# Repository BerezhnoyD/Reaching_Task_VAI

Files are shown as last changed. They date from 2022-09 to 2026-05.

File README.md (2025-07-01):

# ReachOut platform


<p align="center">
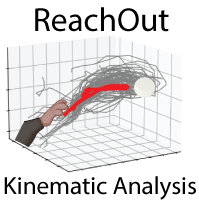
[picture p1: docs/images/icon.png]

</p>

The following project describes the design, fabrication, assembly and use case of the open-source hardware platform for mice reach-to-grasp task training and fine motor skill video analysis. We present the behavioral platform - automated mouse Reaching Box that was designed to be 3D printed and hence easily reproducible. The device is used to train animals to perform reach-to-grasp dexterity task: approach the proximal part of the reaching box and reach for single sugar pellets disposed by motorized feeder disk located in front of the narrow slit. 
This task is used for studying planning and execution of fine motor skills requiring cortical control of the forepaw and finger movement. Behavioral apparatus allows to record the video and track the forepaw and fingers during the reaching movement. Tracking data (performed by DLC networks) can be analyzed further to extract different kinematic parameters (speed, acceleration, jerk, accuracy) and different moments of the reach (start, peak, end) to use them as behavioral keypoints (ex. peri-event analysis).

This repository is accompanying the STARs protocol article describing the fabrication and use of the setup

[Open-source platform for kinematic analysis of mouse forelimb movement](https://star-protocols.cell.com/protocols/3539)

For even more details on installation and use of the Software/Hardware platform visit the 
[Docs Website]

<br>

[][Docs Website]

<br>

The website contains all the documentation and repository contains all the materials to build the mouse reaching task and analyze the data acquired with this task
- *Schematics and blueprints* to assemble the components 
	(**/Article Supplements/**)
- *3D models* for the components of the box 
	(**/ReachingBox_3D_Model/**)
- *Scripts to run the video recording* from the FLIR Camera and logging the data from Arduino 
	(**/Recording toolbox/**)
- *Scripts for the full analysis* dataflow: detecting body parts with DLC and getting the reaching trajectories 
	(**/Analysis toolbox/**)

___

## Installation
***ReachOut*** pipeline can be used with the **behavioral box** to analyze reaching kinematics or as a **standalone application** for kinematic
analysis for the action of your choice (walking, whisker movement, you name it) with certain adaptations. In both cases you
will need to install some software components on your recording/analysis computer. We split the scripts used to two toolboxes with different purpose.

### Recording toolbox
The recording toolbox contains two parts: 
- one on the **Arduino** side (Choose one script from */Arduino/* folder of the repository and uploaded to the microcontroller with the use of **Arduino IDE**). 
- and one on the **PC** side. This Python CLI program is used to record simultaneously from the FLIR camera and from Arduino. 
There are two different programs that can be copies from */FLIR_CPU/* folder of the repository. This part is taken with minor changes from the [PySpin repository], so you should follow the additional instructions listed there. 
We also provide installation instructions on our [Docs Website].

### Analysis toolbox
All the code for analysis toolbox is compiled in the /2D pipeline/ folder. To run different steps of the analysis just run
one of the *ReachOut Notebooks* [^1].
Analysis toolbox is dependent on different Python libraries (ex. DEEPLABCUT, ANIPOSE) and Jupyter Notebook [^2].
DEEPLABCUT (https://github.com/DeepLabCut/DeepLabCut)
ANIPOSE (https://github.com/lambdaloop/anipose)

To make it easier for installation all the dependencies are included in the included **DEEPLABCUT.yml** conda environment file [^3].

___

[^1]: Small library of classes and functions needed to run the kinematic analysis is contained in the *.py files in the same directory and you imported in Notebooks themselves.
[^2]: If you just want to use the Analysis and Visualization notebook on your analyzed videos it should work even in the base Anaconda environment without DLC/Anipose installed. 
[^3]: There are known copmatibility problems on some PCs with the installation of new DLC version that we are trying to fix. Please contact us with any problems you experience.
___
### Troubleshooting

Feel free to read our [Docs Website] and if you still have questions submit a request here or contact the developer directly. 
Contribute, star this repository if you use it and submit an issue for any questions. Let's make it better together.

___

[Docs Website]: https://berezhnoyd.github.io/Reaching_Task_VAI/
[PySpin repository]: https://github.com/neurojak/pySpinCapture
[berezhnoyd.github.io]: https://img.shields.io/badge/Visit_berezhnoyd.github.io-37a779?style=for-the-badge

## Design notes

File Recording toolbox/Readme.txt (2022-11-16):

This folder contains all the programs needed for the behavioral box to work and acquire data.
- Arduino programs for the box controller (in a separate Arduino folder)
- Scripts to run on the computer (in a separate FLIR folder, modified from the PySpin repository)

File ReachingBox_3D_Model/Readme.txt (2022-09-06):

This folder containst all the files needed to built the reaching box:
- 3d files + stl files for printing the plastic angles to hold the Plexiglas sheets together
- 3d files + stl files for mirror hinges (we experimented with different angles so all the angles provided)
- 3d files + stl files for the rotating disk feeder
- blueprints of the plastic sheet dimensions and the overall box

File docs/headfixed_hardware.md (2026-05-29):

---
layout: page
title: Headfixed hardware
parent: Bonus Headfixed setup
nav_order: 7
description: "This is a description of hardware for headfixed setup"
---

# Behavioral setup design

Current protocol is performed with the use of two different systems (shown in the picture below). The one on the right was purchased through [Labeotech](https://www.labeotech.com/product/mouse-head-fixation/),
and the one on the left manufactured in-house using mostly the parts from [ThorLabs](https://www.thorlabs.com/). The list of materials can be found in the source table in the
repository. It should be noted that the first system is designed for the head fixation using the small titanium bars affixed to the skull, while the second is fitted for
the use of headplates, which gives more flexibility in implant design. The second system is easily regulated in height and also can be used for different tasks beyound reaching (ex. rotarod).
 
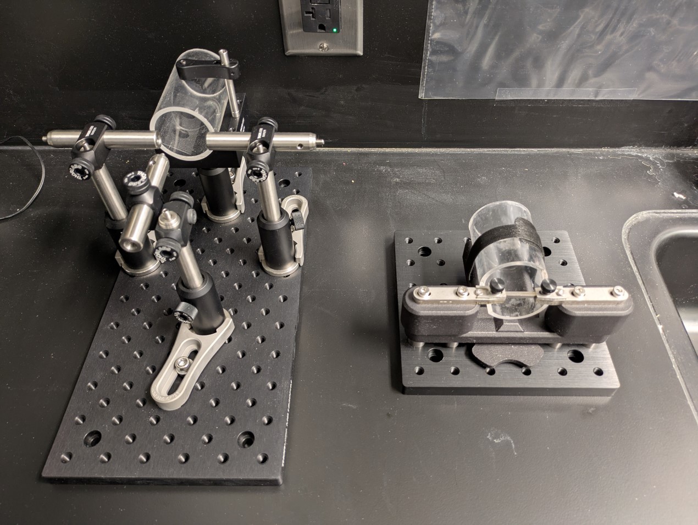
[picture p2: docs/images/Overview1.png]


The system consists of three principal components: 
- Head fixation device with a plastic tube, housing the mouse during the experiment; 
- Motorized water delivery system - linear actuator syringe pump and an XY moving stage with a blunt needle;
- Arduino-based controller performing the programmed experimental protocol (written in C++), interfacing with the touch sensors in the box and providing the master clock signal

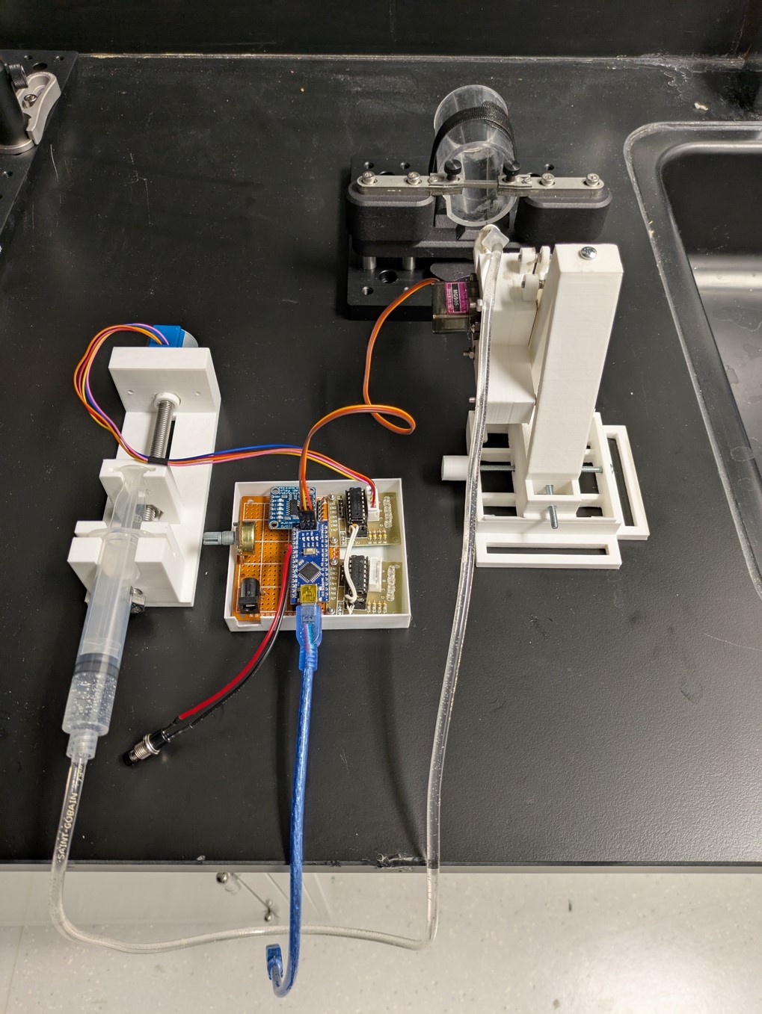
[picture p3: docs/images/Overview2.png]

***The view of the whole system with actuator, water delivery and the controller schematic***

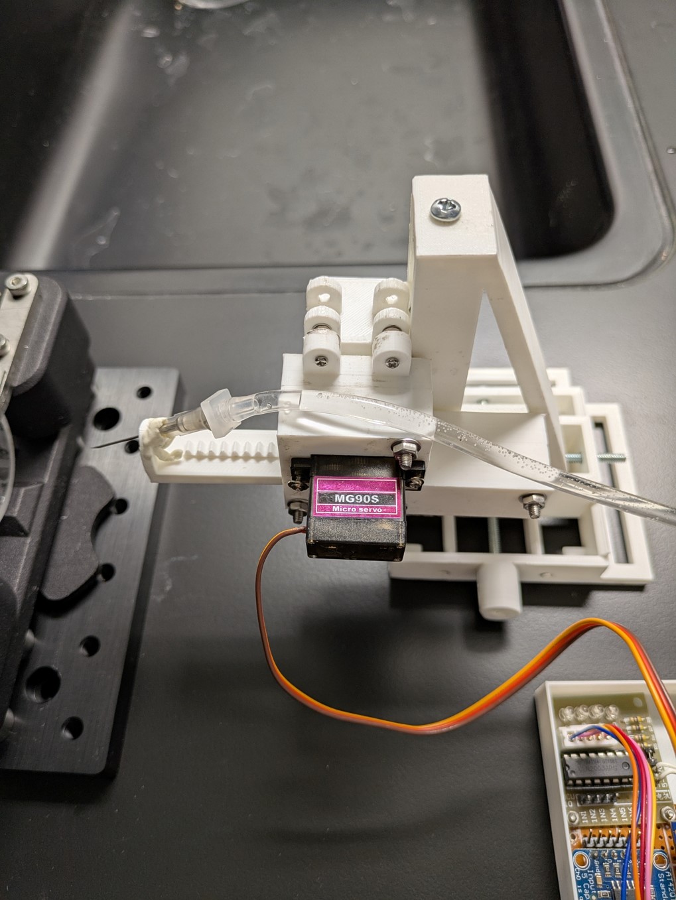
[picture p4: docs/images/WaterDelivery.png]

***Close-up on the water delivery tip on the XY actuator***

The whole water delivery system is 3D printed *.stl* files for printing the plastic components are provided in [this folder] of the repository. You will also need long M2 screws and nuts
to fabricated the metal shafts for XY actuator and M5 screw for the water pump actuator (as a "rail" to move the syringe plunger). 

## Assembly

The custom system is assembled on the optical posts from Thorlabs, which are mounted on the solid heavy base. Two rods mounted perpendicularly are used for holding the head and
are fitted with 3D printed holders for headplates. 
The design for both headplates and the holders can be found in [that folder] of the repository. While holders are 3D printed and simply screwed on the pin of the optical post, 
to manufacture the headplates you will need a laser cutter. If you don't have one you can simply upload the models to one of the online cutting services like [SendCutSend](https://sendcutsend.com/).

The electrical part of the device is largely overlapping with the original ReachOut project (see schematic in the "Hardware part") and is based on the ***Arduino Nano*** 
with two main periferal boards from Adafruit: 
 - ***ULN2003 board*** to control a small BYJ48 stepper motor in the syringe pump
 - ***AT42QT1070*** board connected to the blunted syringe needle to detect touches

***Optional***:  there is also an optional actuator for the syringe needle which is motorized using MG90S servo motor directly connected to Arduino (zoom the picture above for more details).

## Code

As the heart of our training setup is the water delivery system, and it is controlled by Arduino, all the protocols are framed as different programs that can be uploaded on the device.
Those protocols can be found in [code folder] of the repository:
 - HeadFixed_Program
 - HeadFixed_Program_Auto
 - HeadFixed_Program_Manual

There is also some code that can be used if you try to build a headfixed rotarod (based on the rotary encoder with Arduino) with this setup.

[this folder]:(https://github.com/BerezhnoyD/Reaching_Task_VAI/tree/main/HeadFixed_Setup/WaterDelivery/Water_delivery_3d_models/)
[that folder]:(https://github.com/BerezhnoyD/Reaching_Task_VAI/tree/main/HeadFixed_Setup/Headplate_designs/)
[code folder]:(https://github.com/BerezhnoyD/Reaching_Task_VAI/tree/main/HeadFixed_Setup/WaterDelivery/Water_delivery_code/)

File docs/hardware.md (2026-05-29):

---
layout: page
title: Hardware part
nav_order: 3
description: "This is a description of ReachOut behavioral box electronics"

---

## Hardware overview

Here is the design of the whole setup, everything on the box side is controlled by **Arduino**,
and the experiment can be performed event without the the computer, but you will need **the PC** to 
save the streaming data from the camera and the box sensors.  

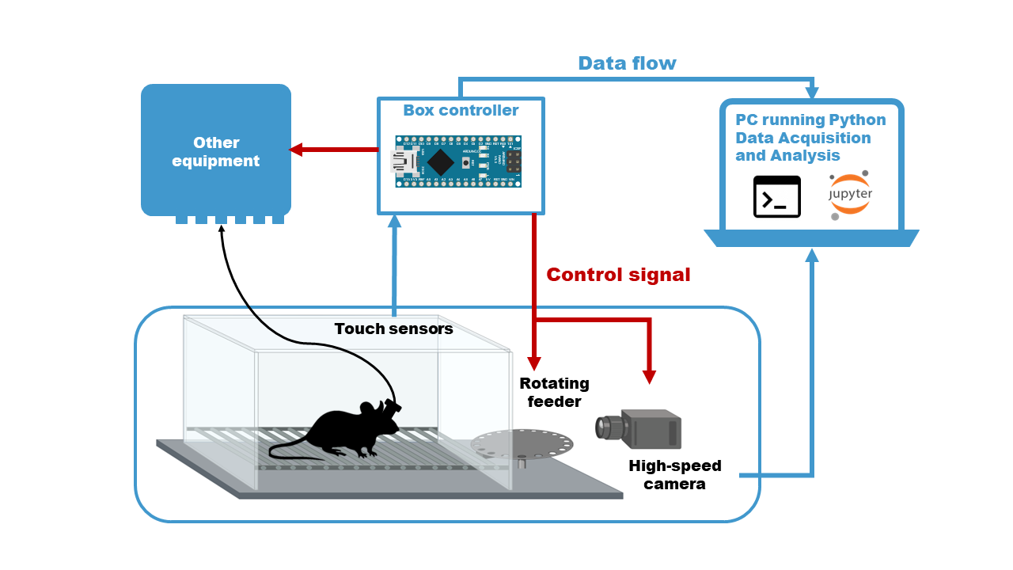
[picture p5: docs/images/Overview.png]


The **control** of the behavioral protocol, all the **stimuli** and **reinforcement** (food pellets) presentation, 
**data logging** from the sensors and video camera stream activation is handled by the custom circuit, connected to all the components of the reaching box. 
The schematics are housed in a small 3d printed box and soldered together on a simple breadboard. Most of the components are ready available cicuit modules, which
you just need to put together (no extensive knowledge of electronics needed).

## Main circuit components

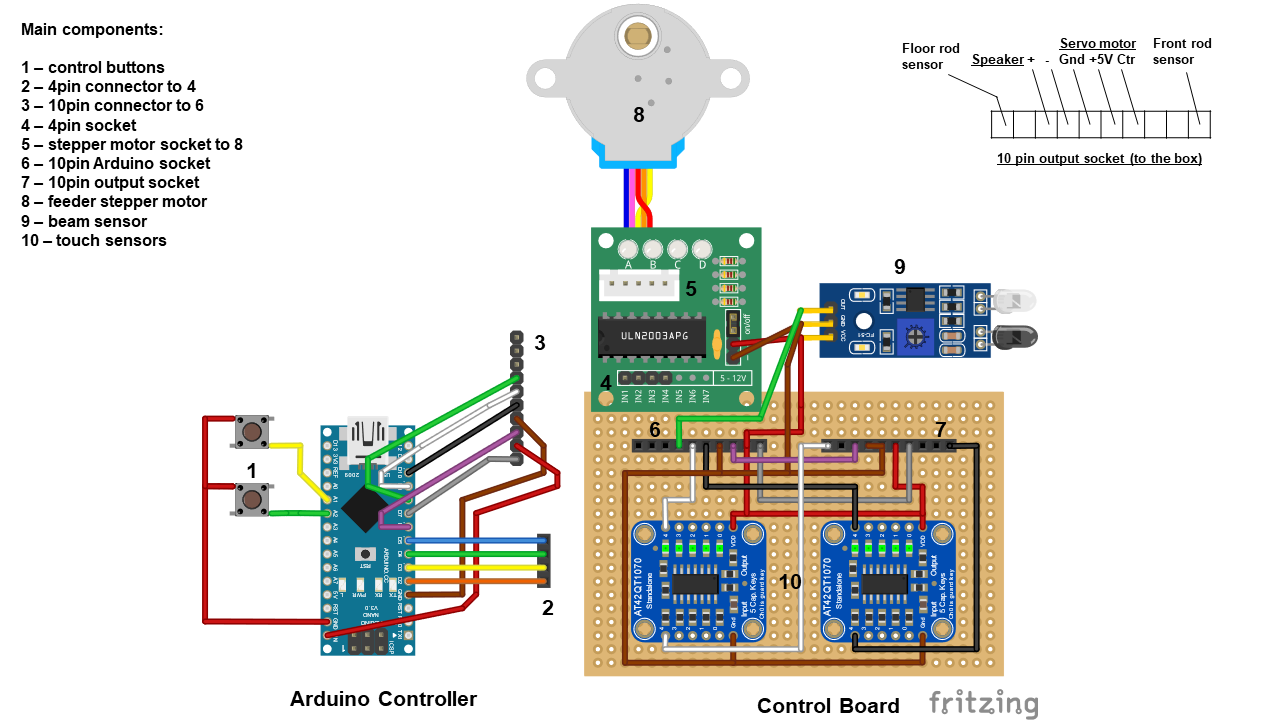
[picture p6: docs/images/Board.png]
  

The same schematics can be found in the Repository and [STAR Protocols] article, supplementary materials.
The main components of the system are the **Arduino Nano** controller autonomously performing the programmed experimental protocol (written in C++ using Arduino IDE) 
with different **Adafruit shields** connected to it. Hence, powered with an external 5V source this behavioral system can be used autonomously for automatic/semi-automatic 
training of mice to perform the reach-to-grasp task, freeing the experimenter from the manual handling of behavioral protocol, and allowing seamless integration with 
*in vivo* electrophysiology recording or other current brain recording/stimulation methods. 

At the same time, connected to the **computer with a USB cable** and a simple 
**Python program** on the computer side this system saves two data streams and allows live monitoring of the data: basic behavioral data from the touch sensors 
(position of the animal, paw placement, time spent in front of the slit, timing and number of trials) and 3d view of the reaching movement (from the front camera and two side mirrors) 
that allows for more sophisticated kinematic analysis of both left and right-hand reaches. 

## Uploading the experimental protocol

The assembled box is programmed with [Arduino IDE] for its use as a standalone device for automated/semi-automated
animal training and behavioral data acquisition. The reaching box can log basic behavioral data (touch/beam sensors)
and is designed to be connected to external devices to trigger in vivo imaging, optogenetic stimulation etc. 
It can stream the synchro signal from the behavioral events recorded by the onboard sensors with millisecond resolution,
which makes it ideally fitted for synchronized behavioral-neurophysiology experiments. With the use of multiple mirrors, 
the system can acquire multiple close-up views for 3d trajectory reconstruction (triangulation) of the reach-to-grasp movement 
with a single high-speed **FLIR camera** when connected to the **desktop PC**. The output of the system is a behavioral video of the 
reaching movements throughout the learning session along with the *.tsv* table of the synchronized data from **Arduino**. 

After a single upload of the program the board will perform it autonomously on every power up without any actions needed from the user. 
To switch to another protocol, we’ll need to upload another program using Arduino IDE. The Arduino programming environment can be downloaded from the
official website [Arduino IDE] and is used to write compile and upload the C++ code for Arduino controllers. 

### List of the programs provided in the repository:
 
1.	***Reaching_Task_Draft*** – basic protocol with initialization for all the components to explore the structure of the program.
2.	***Reaching_Task_Manual*** - Feeder makes one step clockwise or counterclockwise when the experimenter presses the left or right button respectively.
3.	***Reaching_Task_Feeder_Training*** – Feeder takes one step every 10sec while animal is in the front part of the box.
4.	***Reaching_Task_Door_Training*** – If animal is detected in the front part of the box and grabs the elevated front rod, the feeder takes one step and the door blocking the slit opens (need additional servo motor connected, see Fig.3D).
5.	***Reaching_Task_CS_Training***  - If animal is detected in the front part of the box the speaker delivers 5s beep sound (CS trial) with intertrial intervals of 5s (ITI) and if the animal grabs the elevated front rod during this sound (trial) the feeder makes one step and the door blocking the slit opens

## Q&A

If you still have questions after reading this and [STAR Protocols] please let us
know and we list it in this section.

---

[STAR Protocols]: https://star-protocols.cell.com/protocols/3539
[Arduino IDE]: https://www.arduino.cc/en/software

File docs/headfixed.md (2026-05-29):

---
layout: page
title: Bonus Headfixed setup
nav_order: 6
description: "This is a description of the HeadFixed Reaching setup (ReachOut v.2.0)"
has_children: true

---

# ReachOut v.2.0 (Headfixed setup for reaching and treadmill activity)



As a follow-up to the ReachOut project we have developed its full ***headfixed*** counterpart, which we ended up never using. 
But as a bonus here we provide all the details of this side project in a good spirit of open science. We have added a
corresponding section to the original GitHub repository (**/Headfixed_Setup**) and all the contents are described here. Feel free
to hit us with any questions that might save you the trial-and-error process we went through.

## Project overview

The ***contents*** of the project folder in GitHub repository:
 - **WaterDelivery**
	- /Water_delivery_3d_models/ (all the models you need for the water delivery system: DIY pump and actuator)
	- /Water_delivery_code/ (various Arduino programs corresponding to different protocols)
	- /Water_delivery_pictures/ (pictures showing the overview of the system, also Materials Source table) 
	- /Water_delivery_tests/ (pictures and tests for the system)
 - **Headplate designs** (the designs for the headplates for head fixation, modified after A.Ribic [^1] lab)

The ***following sections*** lead you through different parts of the setup: 
 - Hardware, 
 - Electrical Components, 
 - Code to run the protocol, 
 - Device testing and animal training  

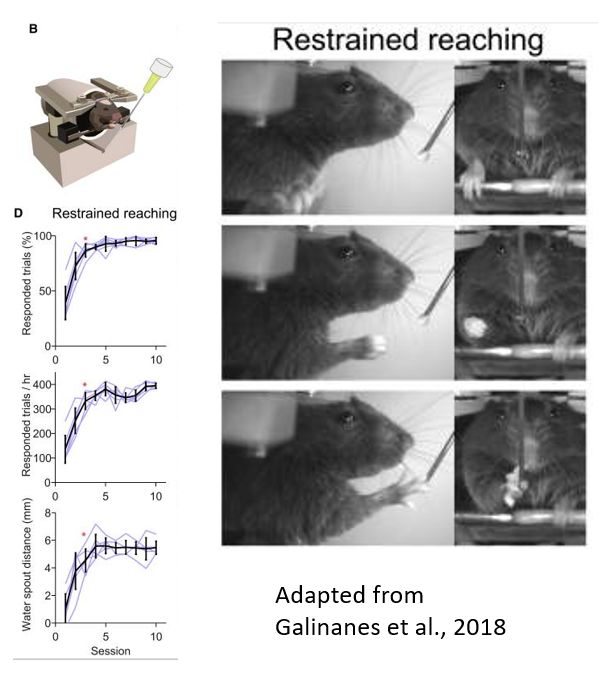
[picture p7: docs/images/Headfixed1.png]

 
This setup allows you to study cortical circuitry of the reaching movement in more detail using 2-photon microscopy or
other methods requiring more stability than you can achieve with freely moving behavior. It is heavily inspired by the one from 
Galinanes 2018 article [^2] and Carlsen 2022 article [^3] so for further details we point you to their work. 
In short, animal is fixed by the head with only the forepaws freely moving, and the water reinforcement is delivered through 
a blunt syringe needle within reaching distance. The distance is gradually increased during training
and the position of the needle changed to shape the proper directional response. 

## About the project

ReachOut is maintained &copy; 2022-{{ "now" | date: "%Y" }} by [Daniil Berezhnoi](https://www.linkedin.com/in/daniil-berezhnoi-a4039844/).
All the materials are OpenSource and Authors would be happy to help you with any questions on the code.

----

[^1]: [Headplate designs from the Ribic lab](https://ribicneurolab.com/headplate-designs)
[^2]: [Directional Reaching for Water as a Cortex-Dependent Behavioral Framework for Mice](https://pubmed.ncbi.nlm.nih.gov/29514103/)
[^3]: [Versatile treadmill system for measuring locomotion and neural activity in head-fixed mice](https://www.sciencedirect.com/science/article/pii/S2666166722005810)

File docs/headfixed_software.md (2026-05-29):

---
layout: page
title: Headfixed software
parent: Bonus Headfixed setup
nav_order: 8
description: "This is a description of software and testing for headfixed setup"
---

# Testing the setup

Initially we have tried to follow the protocol from the Galinanes 2018 article [^1], which includes
gradual shaping of the spontaneous reaching/licking response to water in water-deprived animals. For us
the success of the protocol heavily depended on the level of animal handling (stress response to head restraint),
motivation (water deprivation) and individual differences and the % of animals learned was never more than 50.
Here is the schematic of our initial learning protocol.
 
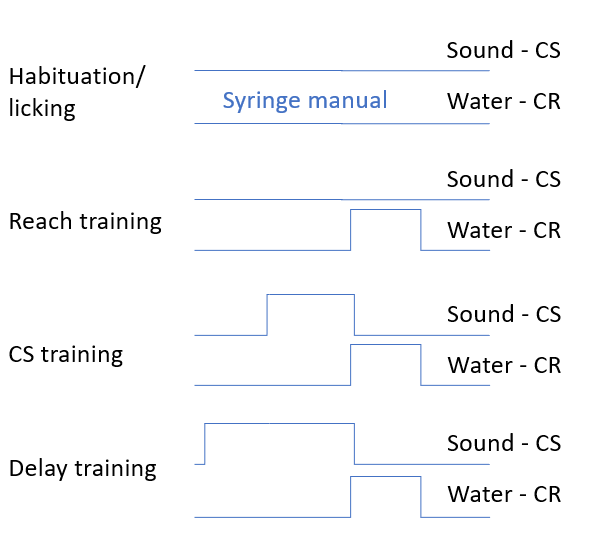
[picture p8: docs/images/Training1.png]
 

Hence, we had to switch to another way of evoking the reaching response that depended less on the internal animal state
and other variables. We actually found the "Pavlovian" way (relying on the innate reaction) to induce reaching more consistent in our hands. 
The innate paw reaction, e.g. grooming/washing response, was consistently induced by touching animal whiskers with the water droplet being delivered.
This reaction, thought initially far from the purposeful reaching for water, can be transformed into a skilled response by the same shaping approach
as was employed in Galinanes 2018 article [^1]. Hence our final protocol looked like this.

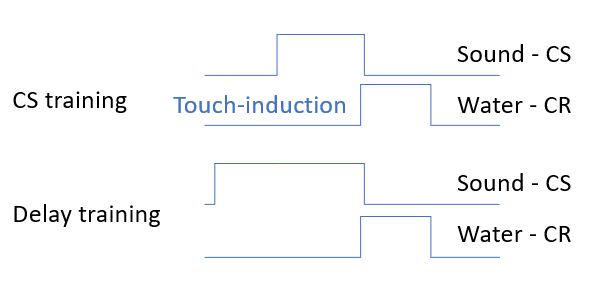
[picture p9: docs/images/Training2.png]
 

## Videos showing different optimization steps 
In the following videos you can see various stages of the protocol and device testing that may give you insights on how to implement the protocol. 
***Note*** that before starting the training protocol animal should be handled and accustomed to the experimenter, to water deprivation, to being restrained in the 
behavioral setup, and licking water from the syringe tip. The device and the protocol should be extensively tested before starting any actual animal work.

First step is to test the water delivery system and determine the optimal ~20-50mkl size of the water droplet before starting any animal work (adjusting the number
of stepper steps and the syringe size mounted in the pump)
<iframe width="600" height="600" src="{{ site.baseurl }}/images/Water1.mp4" frameborder="0" allowfullscreen></iframe>

The goal of the second step is to determine the optimal distance from the snout to the syringe tip (~5mm) to induce the licking and reaching responses
(generally the key is to touch the whiskers at first as it induces the grooming/washing response, and then gradually increase the distance). 
<iframe width="600" height="600" src="{{ site.baseurl }}/images/Water2.mp4" frameborder="0" allowfullscreen></iframe>

The actual training should be performed only when the animal has a stable reaching response and is devoted to pairing up conditioned stimulus (buzzer,
here paired with an LED for illustrative purposes) with the response.
<iframe width="600" height="600" src="{{ site.baseurl }}/images/Water3.mp4" frameborder="0" allowfullscreen></iframe>

----

[^1]: [Directional Reaching for Water as a Cortex-Dependent Behavioral Framework for Mice](https://pubmed.ncbi.nlm.nih.gov/29514103/)

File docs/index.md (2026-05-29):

---
layout: home
title: Home
nav_order: 1
description: "Documentation for the ReachOut project"
permalink: /
---



ReachOut project is an open-source hardware-software platform for analyzing reaching movement kinematics in mice. 
The whole design consists of 3 main parts described here:
{: .fs-6 .fw-200 }
- ***3D printed box*** for training mice to perform reach-to-grasp task & acquire behavioral videos for kinematic analysis
- ***Arduino-based controller*** for executing behavioral protocol & recording animal behavior
- ***ReachOut software (analysis pipeline)*** to analyze videos & perform kinematic analysis on reconstructed forepaw trajectory
{: .fs-6 .fw-200 }


There is an Article in STAR Protocols with all the details and Repository on GitHub with all materials
to recreate the setup
{: .fs-6 .fw-200 }
[View it in the Article][STAR Protocols]{: .btn .btn-primary .fs-5 .mb-4 .mb-md-0 .mr-2 }
[View it on GitHub][ReachOut]{: .btn .fs-5 .mb-4 .mb-md-0 }
 
{: .warning }
> This website documents the features of the current `main` branch accompanying the STARs Protocol article. For the code described in the article use
> alpha or beta release in the [ReachOut] repository

---

### Getting Started
Did you know that mice are pretty good at using their forepaws? Well, probably you do
and can skip the [Science background](#science-background) section and go straight to [Project overview](#project-overview)
or to one of the sections provided in the docs (*Navigation on the left sidebar*).



But how to dissect and study this complex movement? 
We tried to provide the comprehensive solution to this problem that can be
implemented in-lab with a little background knowledge in *3d printing, Arduino and Python Coding*.
  
All the installation instructions are currently in the [Software part](#software.html) section. 
You can use the analysis part separately for your project by copying the Jupyter Notebooks.

### Science background
Reach-to-grasp task in rodents first developed by Ian Whishaw [^1] has recently became the gold standard for the study of fine motor behavior in rodents.
The structure of the movement and the neurocircuitry behind it can be well translated between rodents and higher primates including humans [^2][^3] which makes this task
very popular for the study of cortical motor control. There is an increasing use of reach-to-grasp task along current neurophysiological tools like 2-photon imaging
or optogenetics for the study of neural activity during execution of the planned motor command [^4]. However, there are not many designs available for the reach-to-grasp task in freely behaving mice. 

With the dawn of DIY electronic kits (**Arduino**) and stereolithography 3D printer technology (**OpenCAD**) we see the field of open-source behavioral box design rapidly expanding and
being a major driver for neuroscience discoveries. There are multiple designs for Skinner boxes and rodent operant chambers proposed by different laboratories. However, there are fewer 
solutions to study fine motor skills, probably due to the difficulties in *precise presentation of the reinforcement* and *quantifying the kinematics* of the small animal movements. 
The second problem has been recently solved with the use of deep-learning video analysis [DeepLabCut]. However, the solutions specifically tailored for the behavior-neurophysiology coupling often use
head-fixed animals and focused on precise synchronization of the animal behavior, heavily constrained, with the neurophysiology recording. 
Training animals in such setups can be *problematic and labor-intensive*. On the other side, apparatuses proposed to study reaching in freely behaving animals, 
following the line of operant boxes research, usually lack the precision and time resolution needed to synchronize with external devices used in neurophysiology research. Moreover, research with 
automatic learning boxes, even ReachingBots [^5], generally focus on simple metrics like the number of trials and success rate of reaching and overlook more sophisticated kinematic analysis which requires better video quality, 
precision and post-processing of the behavioral data. Thus, there is always a tight balance between the *open-source (ease of manufacture)* and *research-grade (temporal precision)* needed for neurophysiology 
and precise kinematic studies.
  
***Trying to fill this gap we have developed a comprehensive hardware-software setup for mice, using the current state-of-the-art solutions in 3D printing and DNN data analysis and made it accessible to the large open-science community.***

### Project overview
This website describes the basics of design, fabrication, assembly and use case for the open-source hardware platform
for mice reach-to-grasp task training and fine motor skill video analysis. You are free to use either the [Software part](#software.html)
of this project for kinematic analysis ***(ReachOut pipeline)*** on the videos from your setup or build the whole behavioral apparatus setup 
using the instructions provided in the [STAR Protocols] article.

***Behavioral apparatus*** - automated mouse Reaching Box that is 3D printed and hence easily reproducible. 
The device is used to train animals to perform reach-to-grasp dexterity task: approach the proximal part of the reaching box
and reach for single sugar pellets disposed by motorized feeder disk located in front of the narrow slit. 
This task is used for studying planning and execution of fine motor skills requiring cortical control of the forepaw and finger movement. 
The semi-automated setup allows to record the video and track the forepaw and fingers during the reaching movement. 

***Hardware*** used in the design of the task, aside from the high-speed FLIR camera, 
consists of readily available open-source components that can be acquired relatively 
cheap or fabricated with the use of stereolithography 3D printer. 

The [ReachOut] repository contains all the materials to build the mouse reaching task and analyze the data acquired with this task
- 3D models for the components of the box
- Schematics for the reaching box Arduino-based controller
- Scripts to run the video recording from the FLIR Camera and logging the data from Arduino
- Scripts for the full analysis dataflow: detecting body parts with DLC and getting the reaching trajectories

***Analysis software*** can be used with the behavioral box to analyze reaching kinematics or as a standalone application for kinematic
analysis for the action of your choice (walking, whisker movement, you name it) in your project with certain adaptations. The aim of this part
is to simplify keypoint tracking (performed by DLC networks), reviewing tracking results along with the videos and extract different kinematic parameters 
(speed, acceleration, jerk, accuracy) and different moments of the reach (start, peak, end) to use them as behavioral keypoints (ex. peri-event analysis).

We gathered all the code in a series of annotated [Jupyter Notebooks] for you to use. All the necessary
libraries can be installed using provided *DEEPLABCUT.yml* environment file for **Anaconda**.
For the quick overview and instructions go straight to [Software part](#Software part) section.

## About the project

ReachOut is maintained &copy; 2022-{{ "now" | date: "%Y" }} by [Daniil Berezhnoi](https://www.researchgate.net/profile/Daniil-Berezhnoy).
All the materials are OpenSource and Authors would be happy to help you with any questions on the code.

----

[^1]: [The structure of skilled forelimb reaching in the rat: A proximally driven movement with a single distal rotatory component](https://www.sciencedirect.com/science/article/pii/016643289090053H#:~:text=(1)%20Most%20of%20the%20first,the%20midline%20of%20the%20body.).
[^2]: [Post-stroke kinematic analysis in rats reveals similar reaching abnormalities as humans](https://www.nature.com/articles/s41598-018-27101-0)
[^3]: [Quantitative kinematic characterization of reaching impairments in mice after a stroke](https://pubmed.ncbi.nlm.nih.gov/25323462/)
[^4]: [Online control of reach accuracy in mice](https://www.ncbi.nlm.nih.gov/pmc/articles/PMC7814908/)
[^5]: [ReachingBot: An automated and scalable benchtop device for highly parallel Single Pellet Reach-and-Grasp training and assessment in mice](https://www.sciencedirect.com/science/article/pii/S0165027023001279?via%3Dihub)

[STAR Protocols]: https://star-protocols.cell.com/protocols/3539
[DeepLabCut]: https://github.com/DeepLabCut/DeepLabCut/
[Anipose Lib]: https://github.com/lambdaloop/aniposelib/
[ReachOut]: https://github.com/BerezhnoyD/Reaching_Task_VAI/
[Jupyter Notebooks]: https://github.com/BerezhnoyD/Reaching_Task_VAI/tree/main/Analysis toolbox/2D pipeline/
[Just the Docs]: https://just-the-docs.github.io/just-the-docs/
[GitHub Pages]: https://docs.github.com/en/pages
[README]: https://github.com/just-the-docs/just-the-docs-template/blob/main/README.md
[Jekyll]: https://jekyllrb.com
[GitHub Pages / Actions workflow]: https://github.blog/changelog/2022-07-27-github-pages-custom-github-actions-workflows-beta/
[use this template]: https://github.com/just-the-docs/just-the-docs-template/generate

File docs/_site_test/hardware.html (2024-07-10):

Skip to main content

ReachOut kinematic analysis

This site uses Just the Docs (https://github.com/just-the-docs/just-the-docs), a documentation theme for Jekyll.

## Hardware overview

Here is the design of the whole setup, everything on the box side is controlled by Arduino, and the experiment can be performed event without the the computer, but you will need the PC to save the streaming data from the camera and the box sensors.



The control of the behavioral protocol, all the stimuli and reinforcement (food pellets) presentation, data logging from the sensors and video camera stream activation is handled by the custom circuit, connected to all the components of the reaching box. The schematics are housed in a small 3d printed box and soldered together on a simple breadboard. Most of the components are ready available cicuit modules, which you just need to put together (no extensive knowledge of electronics needed).

## Main circuit components



The same schematics can be found in the Repository and STAR Protocols (https://star-protocols.cell.com/protocols/3539) article, supplementary materials. The main components of the system are the Arduino Nano controller autonomously performing the programmed experimental protocol (written in C++ using Arduino IDE) with different Adafruit shields connected to it. Hence, powered with an external 5V source this behavioral system can be used autonomously for automatic/semi-automatic training of mice to perform the reach-to-grasp task, freeing the experimenter from the manual handling of behavioral protocol, and allowing seamless integration with in vivo electrophysiology recording or other current brain recording/stimulation methods.

At the same time, connected to the computer with a USB cable and a simple Python program on the computer side this system saves two data streams and allows live monitoring of the data: basic behavioral data from the touch sensors (position of the animal, paw placement, time spent in front of the slit, timing and number of trials) and 3d view of the reaching movement (from the front camera and two side mirrors) that allows for more sophisticated kinematic analysis of both left and right-hand reaches.

## Uploading the experimental protocol

The assembled box is programmed with Arduino IDE (https://www.arduino.cc/en/software) for its use as a standalone device for automated/semi-automated animal training and behavioral data acquisition. The reaching box can log basic behavioral data (touch/beam sensors) and is designed to be connected to external devices to trigger in vivo imaging, optogenetic stimulation etc. It can stream the synchro signal from the behavioral events recorded by the onboard sensors with millisecond resolution, which makes it ideally fitted for synchronized behavioral-neurophysiology experiments. With the use of multiple mirrors, the system can acquire multiple close-up views for 3d trajectory reconstruction (triangulation) of the reach-to-grasp movement with a single high-speed FLIR camera when connected to the desktop PC. The output of the system is a behavioral video of the reaching movements throughout the learning session along with the .tsv table of the synchronized data from Arduino.

After a single upload of the program the board will perform it autonomously on every power up without any actions needed from the user. To switch to another protocol, we’ll need to upload another program using Arduino IDE. The Arduino programming environment can be downloaded from the official website Arduino IDE (https://www.arduino.cc/en/software) and is used to write compile and upload the C++ code for Arduino controllers.

### List of the programs provided in the repository:

1. Reaching_Task_Draft – basic protocol with initialization for all the components to explore the structure of the program.
2. Reaching_Task_Manual - Feeder makes one step clockwise or counterclockwise when the experimenter presses the left or right button respectively.
3. Reaching_Task_Feeder_Training – Feeder takes one step every 10sec while animal is in the front part of the box.
4. Reaching_Task_Door_Training – If animal is detected in the front part of the box and grabs the elevated front rod, the feeder takes one step and the door blocking the slit opens (need additional servo motor connected, see Fig.3D).
5. Reaching_Task_CS_Training - If animal is detected in the front part of the box the speaker delivers 5s beep sound (CS trial) with intertrial intervals of 5s (ITI) and if the animal grabs the elevated front rod during this sound (trial) the feeder makes one step and the door blocking the slit opens

## Q&A

If you still have questions after reading this and STAR Protocols (https://star-protocols.cell.com/protocols/3539) please let us know and we list it in this section.

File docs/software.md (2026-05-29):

---
layout: page
title: Software part
nav_order: 4
description: "This is a description of ReachOut software"
has_children: true

---

# Triangulation and analysis of behavioral videos

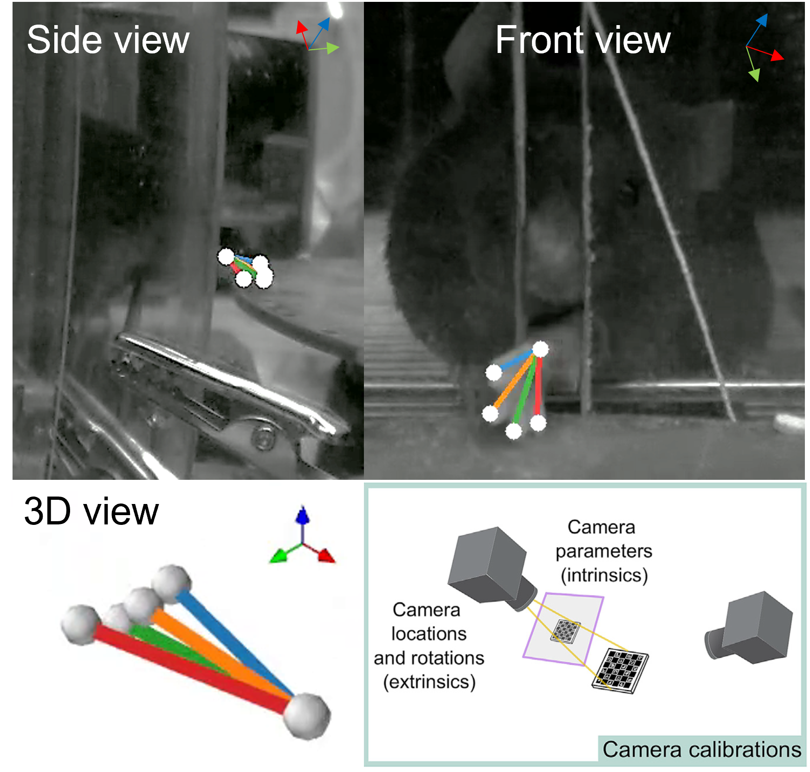
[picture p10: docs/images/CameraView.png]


In addition to the hardware part, we provide the complementary software data analysis pipeline which can be performed off-line with the acquired videos. Python package for the 3d trajectory reconstruction and kinematic analysis is organized in classes and modules implemented in a series of Jupyter Notebooks and based on the state-of-the-art solutions for the markerless pose estimation as well as original code
 - [DeepLabCut] is used for intial tracking using pretrained ResNet architecture (& training it). 
 - [Anipose Lib] is used for the 3d triangulation part to restore the action in absolute coordinates (mm).
 - [ReachOut] is our humble code contribution and is used for all the analysis on kinematic traces.
 
___ 
 
## ReachOut kinematic analysis pipeline

The [ReachOut] pipeline can be used separately on your own videos and guides the user through the number of steps to extract the parts from the video, track and triangulate the points of interest (paw, fingers), cluster the reaches, visualize and compare basic kinematic parameters for different reaching categories. User has the ability to export the final data on the kinematics (scalars for each reach) and reaching timestamps as a *.h5/.csv table for further analysis or synchronization with his own pipeline.

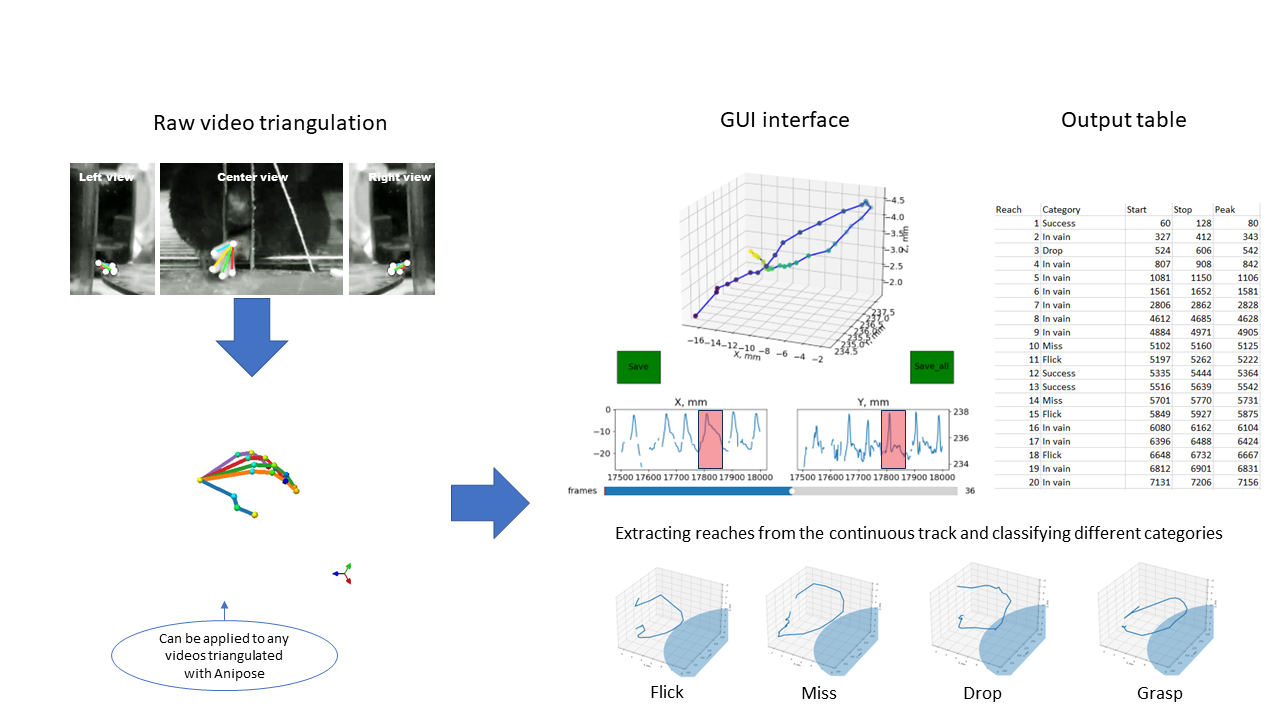
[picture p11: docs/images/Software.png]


Analysis pipeline consists of extracting the parts from the video, 
tracking and triangulating the points of interest (paw, fingers), clustering the reaches, 
visualizing and comparing basic kinematic parameters between different reaching categories.
We suggest copying the whole folder
- **2D pipeline** or
- **3D pipeline**
 
from the [Analysis Toolbox], nd then running the Notebooks using **Jupyter**

```python
> cd path\to\the scripts\
> conda activate DEEPLABCUT
> jupyter notebook
```
___

## Using ReachOut analysis pipeline

{: .note }
There are two pipelines provided - one for 3d analysis and reconstruction, and a simpler 2d one, working with only one 
video (single camera view). We mention the differences in the following sections and suggest to start with a simpler one
if your experiment doesn't specfically require triangulation and representation of coordinates in absolute space (in *mm*).

The Notebooks are split by their function:
**ReachOut - Tracking** guides the user throught the necessary steps for tracking the points of interest
- Cutting the video acquired with FLIR camera into three parts - *specific for our setup with two mirrors*
- Opening the DeepLabCut interface window and running through the full pipeline to track the points of interest
- Updating the csv output from DeepLabCut with absolute position for our reference points
- Using the code from Anipose lib and preprecorded calibration videos to triangulate the points - *specific for our setup with two mirrors*

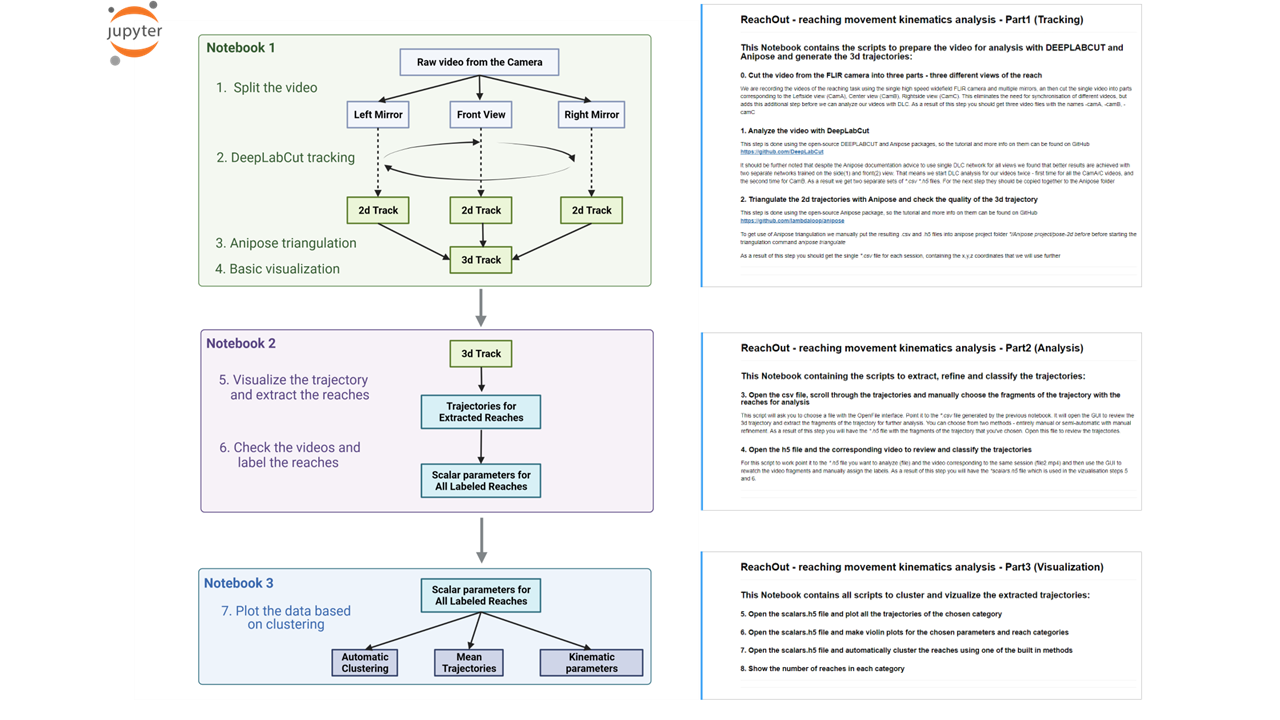
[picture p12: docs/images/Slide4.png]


***Here are the main steps as described in the Notebooks***

___

### ReachOut - Tracking
**Provides all the scripts to process the behavioral videos and get to the .csv file with** 

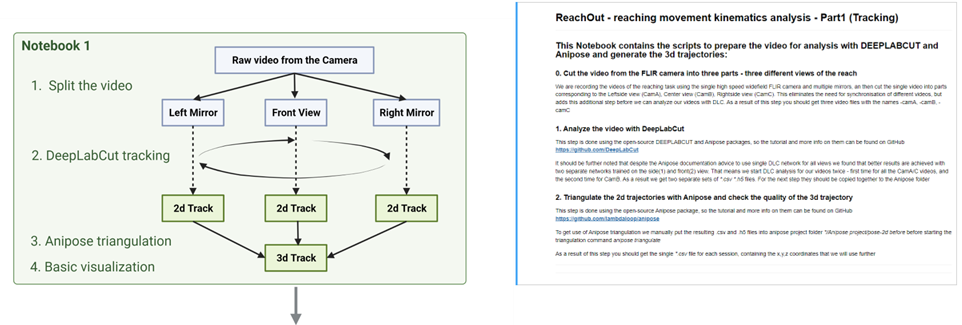
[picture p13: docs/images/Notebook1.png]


0. Cut the video from the FLIR camera into three parts - three different views of the reach
> We are recording the videos of the reaching task using the single high speed widefield FLIR camera and multiple mirrors. 
> So the first part is to cut single video into parts corresponding to the Rightside view (CamA), Center view (CamB), Leftside view (CamC) 
> with respect to the animal paw. This eliminates the need for synchronisation of different videos, but adds this additional step before we
> can analyze our videos with DLC. As a result of this step you should get three video files with the names -camA, -camB, -camC 

1. Analyze the video with DeepLabCut
> This step is performed using open-source [DeepLabCut] package, the tutorial and more info on which can be found on GitHub.
> In short, the first command should launch DeepLabCut interface which guides you through creating the network, training dataset from your videos
> (selecting subset of frames and manually labeling the points of interest), training & evaluating the network and finally applying it to all your videos. 
> The final output should be a *.csv* file for each video with coordinates (in pixel dimensions) for all the points tracked by the network. 
> We added some code to open, check this table and insert necessary columns with static points for triangulation.

{: .warning }
It should be further noted that despite the Anipose documentation advice to use single DLC network for all views we found that better results
are achieved with two separate networks trained on the side(1) and front(2) view. That means we start DLC analysis for our videos twice - first 
time for all the CamA/C videos, and the second time for CamB. As a result we get two separate sets of _*.csv *.h5_ files. 
For the next step they should have the same name with the difference of last prefix "A,B,C" and copied together to one folder accessible by this Notebook. 
***Not needed if using simpler 2D pipeline without triangulation***

2. Triangulate the 2d trajectories with Anipose and check the quality of the 3d trajectory 
> This step is done using the open-source Anipose package, so the tutorial and more info on them can be found on GitHub
> Here we provide the code snippet (from [Anipose Lib]) to calibrate the camera intrinsics using prerecorded videos or checkerboard pattern 
> and use the resulting *calibration.toml* file to triangulate coordinates for the paw in absolute space.
>
> If you want to use Anipose interface for triangulation you should manually put the resulting .csv and .h5 files into anipose project folder 
> _*/Anipose project/pose-2d before_ before starting the triangulation command _anipose triangulate_
>
> As a result of this step you should get the single _*.csv_ file for each session, containing absolute x,y,z coordinates, that we will use further  
***Not needed if using simpler 2D pipeline without triangulation***

___

### ReachOut - Analysis
**Provides multiple gui snippets to manually segment and annotate the results from DeepLabCut**

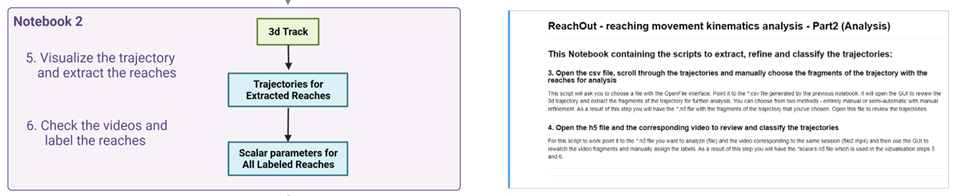
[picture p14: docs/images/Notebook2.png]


- Manually scroll through DeepLabCut tracking coordinates, plot them and choose the segments for kinematic analysis (*reaches in our case*)
- Load the selected parts of the trajectory and manually annotate them from watching the corresponding parts of the video (*we defined different reaching categories*)

3. Open the *.csv* file, scroll through the trajectories and manually choose the fragments of the trajectory (*with the reaches*) for analysis
> This script will ask you to choose a file with the OpenFile interface. Point it to the *.csv file generated by the previous notebook. 
> It will open the GUI to review the 2d trajectory with time used as a 3rd dimension and extract the fragments of the trajectory for further analysis. 
> As a result of this step you will have the *.h5 file with the fragments of the trajectory that you've chosen. Open this file to review the trajectories.

Small video showing the workflow

<iframe width="960" height="520" src="{{ site.baseurl }}/images/Step3.mp4" frameborder="0" allowfullscreen></iframe>

{: .note }
In cotrast to the standard 3D pipeline (tracking_split), 2D relies on the different script (tracking_split_2d), all other steps are the same, but with the 
time substituting Z-dimension in the 3D plot, that way you basically see the change in 2d trajectory with time.

4. Open the h5 file and the corresponding video to review and classify the trajectories
> This script is made to load the selected parts of the trajectory and manually annotate them from watching the corresponding parts of the video. 
> For this script to work point it to the _*.h5_ file you want to analyze (file) and the video corresponding to the same session (file2.mp4) and then 
> use the GUI to rewatch the video fragments and manually assign the labels. As a result of this step you will have the _*scalars.h5_ file which is 
> used in the vizualisation steps 5 and 6.

<iframe width="960" height="520" src="{{ site.baseurl }}/images/Step4.mp4" frameborder="0" allowfullscreen></iframe>

___

### ReachOut - Visualization
**Provides the user with multiple ways to visualize the data and kinematic parameters**



- Look at superimposed trajectories for the chosen category of action - *reaches in our case*
- Look at the violin plots for different kinematic parameters for the chosen category of action
- Cluster the actions based on the chosen set of parameters

5. Open the scalars.h5 file and plot all the trajectories of the chosen category
> This snippet shows all reaches in the chosen category as Timeseries for visual inspection and analysis. 
> From the lists you can choose the category of reaches and the type of data to plot.

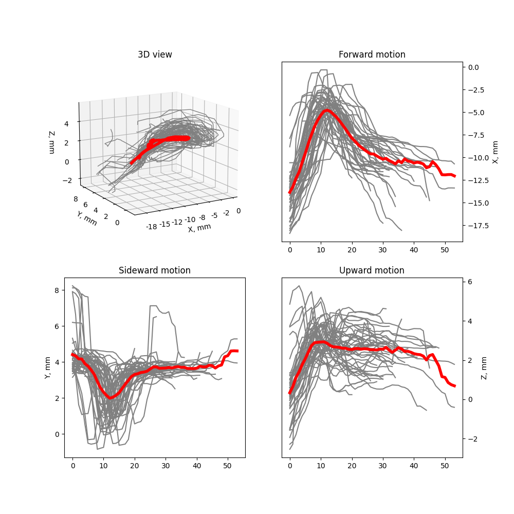
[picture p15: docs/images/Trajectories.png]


6. Open the scalars.h5 file and make violin plots for the chosen parameters and reach categories  

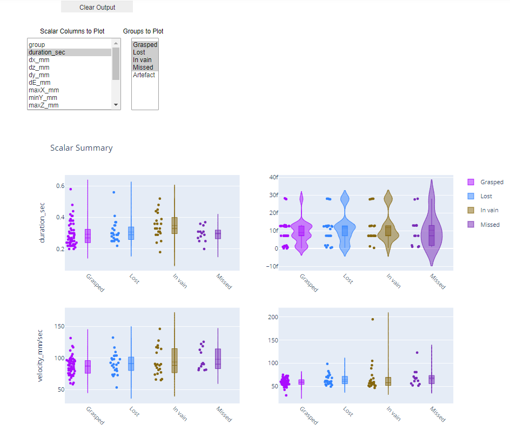
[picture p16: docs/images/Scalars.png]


7. Open the scalars.h5 file and automatically cluster the reaches using one of the built in methods

8. Show the number of reaches in each category

___

## Q&A

If you still have questions after reading this and [STAR Protocols] please let us
know and we list it in this section.

---

[STAR Protocols]: https://star-protocols.cell.com/protocols/3539
[DeepLabCut]: https://github.com/DeepLabCut/DeepLabCut
[ReachOut]: https://github.com/BerezhnoyD/Reaching_Task_VAI/
[Recording Toolbox]: https://github.com/BerezhnoyD/Reaching_Task_VAI/tree/main/Recording%20toolbox
[Analysis Toolbox]: https://github.com/BerezhnoyD/Reaching_Task_VAI/tree/main/Analysis%20toolbox
[Anipose Lib]: https://github.com/lambdaloop/anipose
[PySpin]: https://github.com/neurojak/pySpinCapture

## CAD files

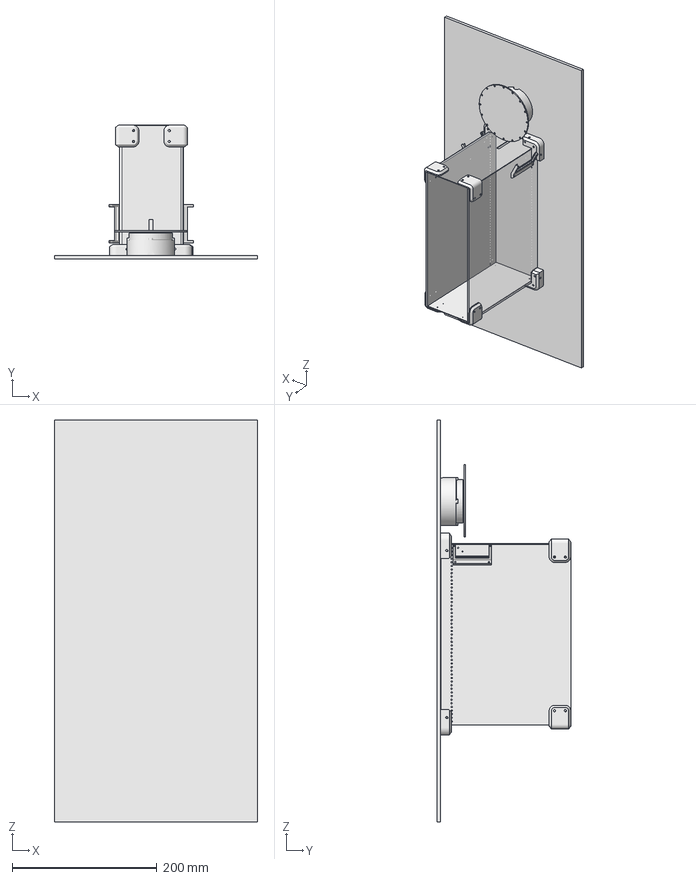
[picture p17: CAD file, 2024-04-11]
ReachingBox_3D_Model/Reaching Box/Box assembled.FCStd
281.3 x 185.2 x 556.1 mm
BackWall-BodyPad
FrontWall-BodyPad
SideWall-BodyPad
Disc feeder-Compound
Top angle
Support-Print
SideWall-BodyPad001
Bottom angle
Top angle001
Top angle002
Top angle003
Bottom angle001
Bottom angle002
Bottom angle003
Hinge for the mirror-27
Hinge for the mirror-028

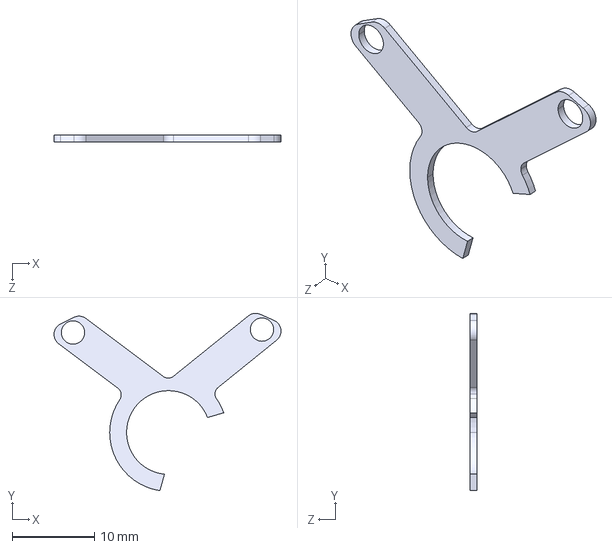
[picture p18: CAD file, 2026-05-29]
HeadFixed_Setup/Headplate_designs/semi circle (1).STEP
27.7 x 21.6 x 0.813 mm

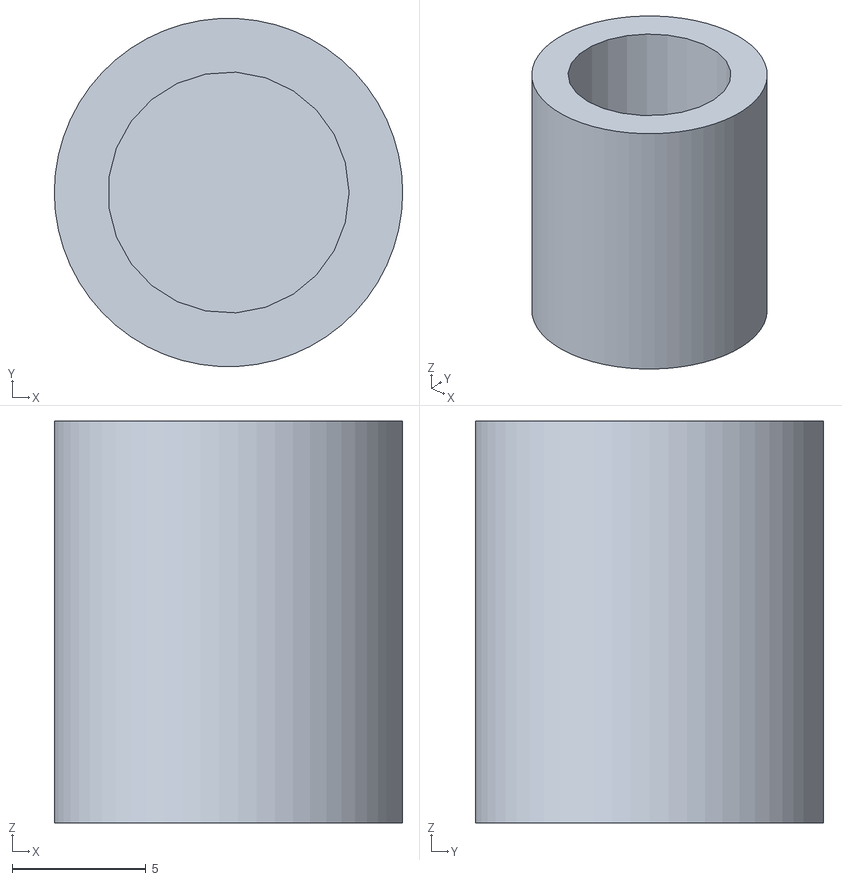
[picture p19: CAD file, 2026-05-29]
HeadFixed_Setup/WaterDelivery/Water_delivery_3d_models/delivery_motor2thread (1).stl
13.0 x 13.0 x 15.0

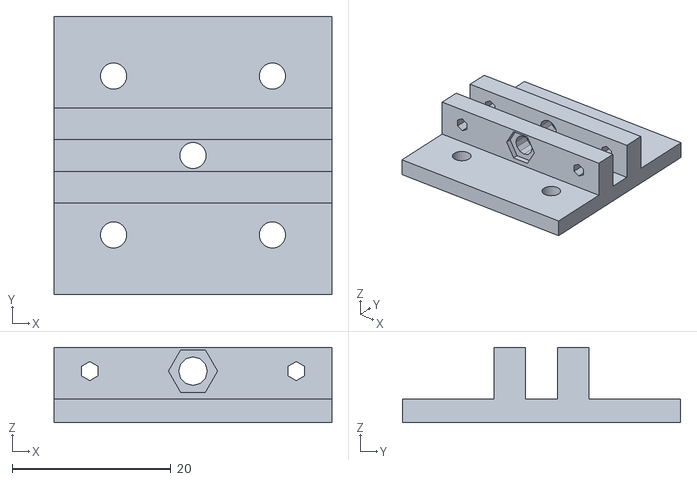
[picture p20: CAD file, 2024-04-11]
ReachingBox_3D_Model/Feeder V2/x-stage-top-union003.stl
35.0 x 35.0 x 9.50

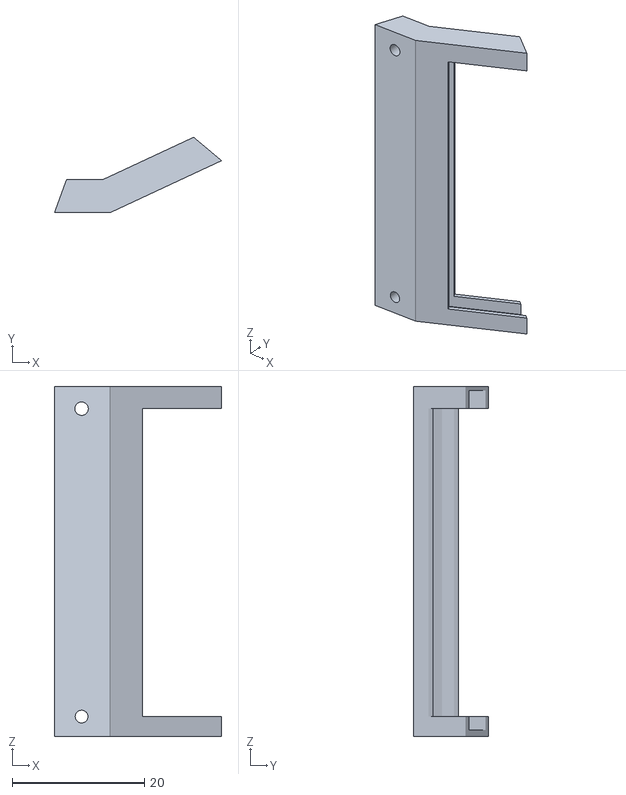
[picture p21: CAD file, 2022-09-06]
ReachingBox_3D_Model/Hinge for the mirror-25.stl
25.3 x 11.4 x 53.0

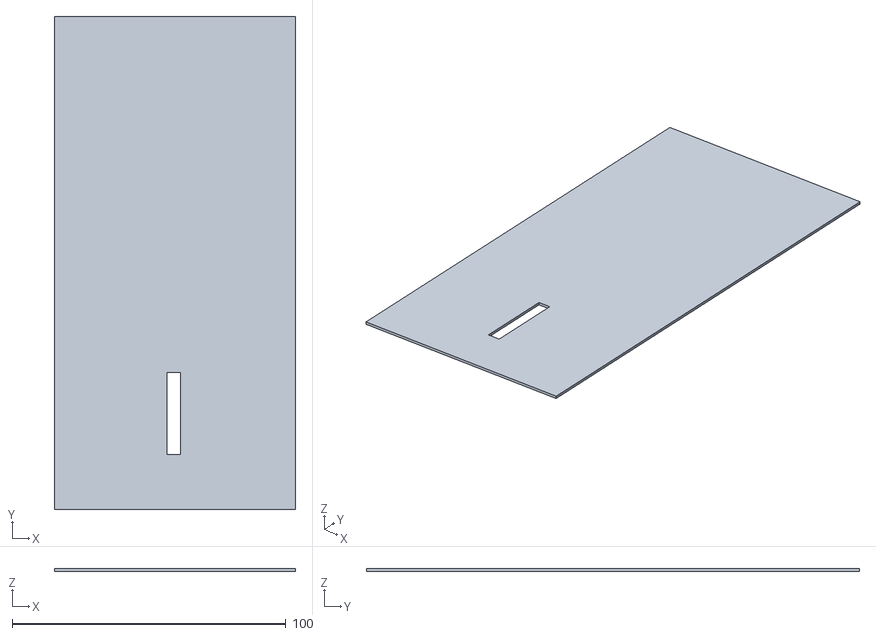
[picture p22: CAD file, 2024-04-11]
ReachingBox_3D_Model/Reaching Box/FrontWall-BodyPad.stl
88.0 x 180.0 x 1.00

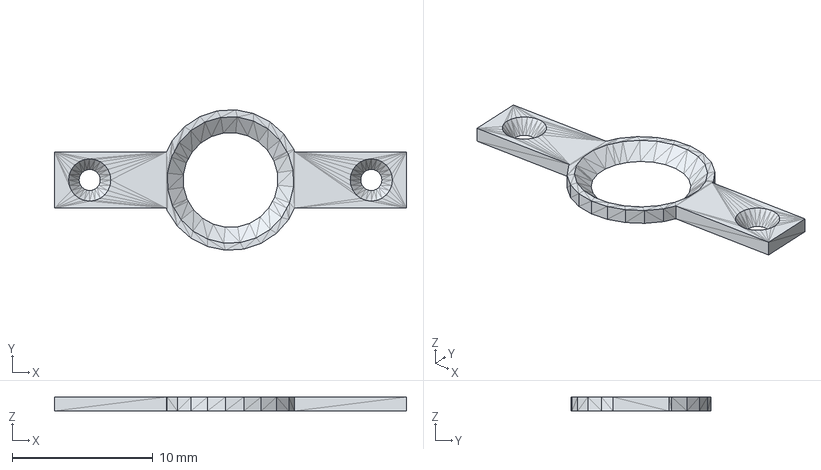
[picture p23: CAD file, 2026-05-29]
HeadFixed_Setup/Headplate_designs/headplate.step
25.0 x 9.97 x 1 mm

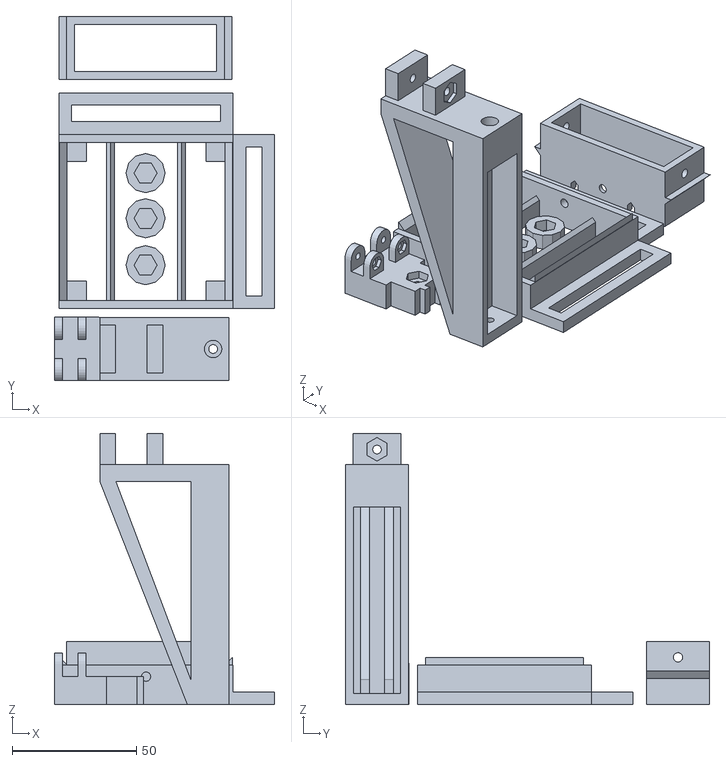
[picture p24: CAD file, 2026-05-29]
HeadFixed_Setup/WaterDelivery/Water_delivery_3d_models/micropositioner_combined (1).stl
88.4 x 146.4 x 108.9

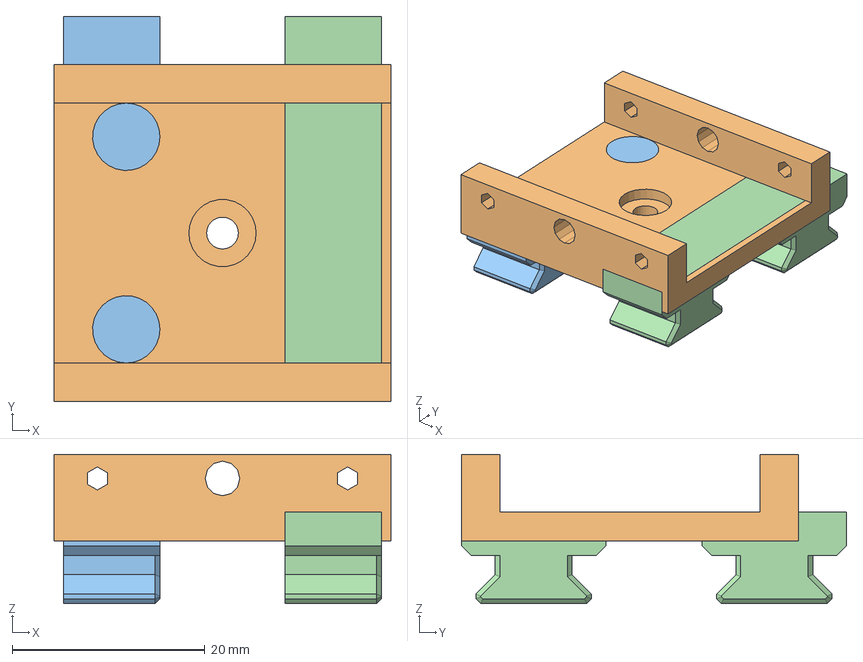
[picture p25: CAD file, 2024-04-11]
ReachingBox_3D_Model/Feeder V2/XYstage.FCStd
35.0 x 40.0 x 15.5 mm
x-stage1-union003
LinearRailTest-Slider-short-test
LinearRailTest-Slider-short-test001

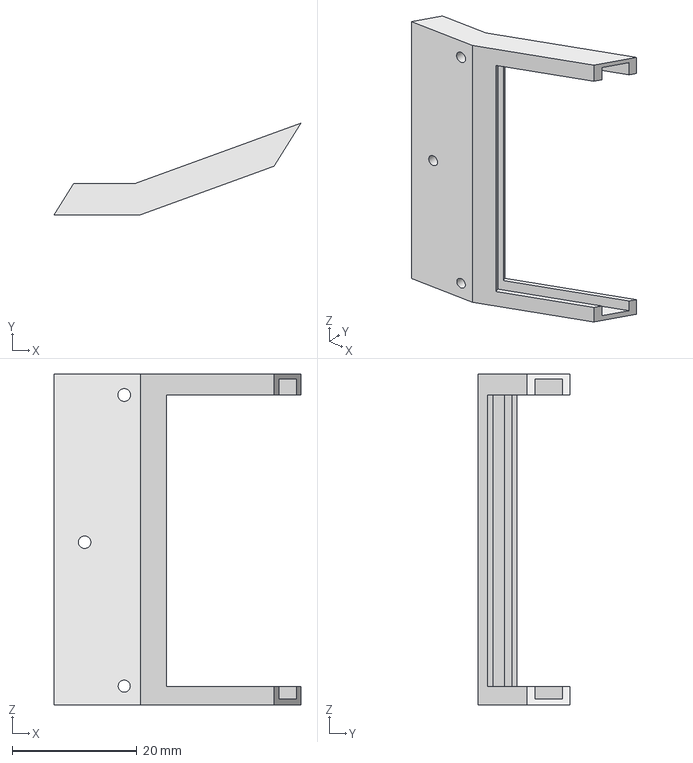
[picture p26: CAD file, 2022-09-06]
ReachingBox_3D_Model/Hinge for the mirror2.FCStd
39.5 x 14.7 x 53.0 mm

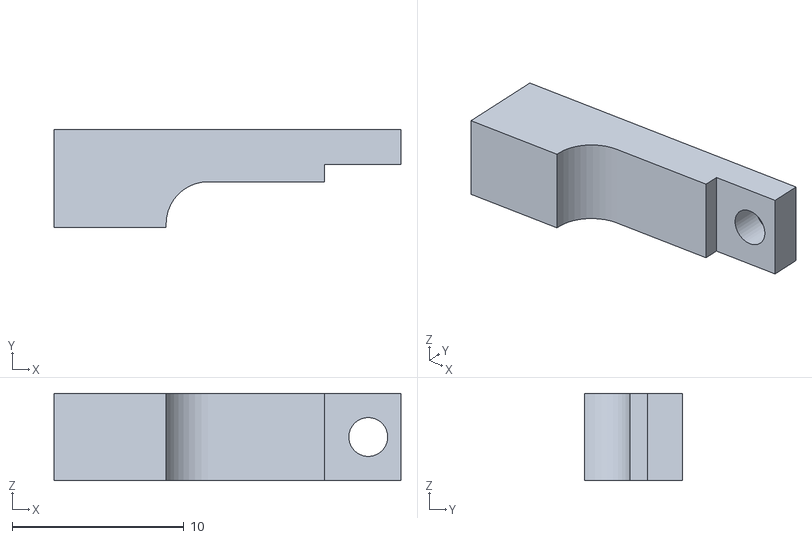
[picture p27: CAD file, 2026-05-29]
HeadFixed_Setup/Headplate_designs/small holder (1) (2).STL
20.2 x 5.72 x 5.08

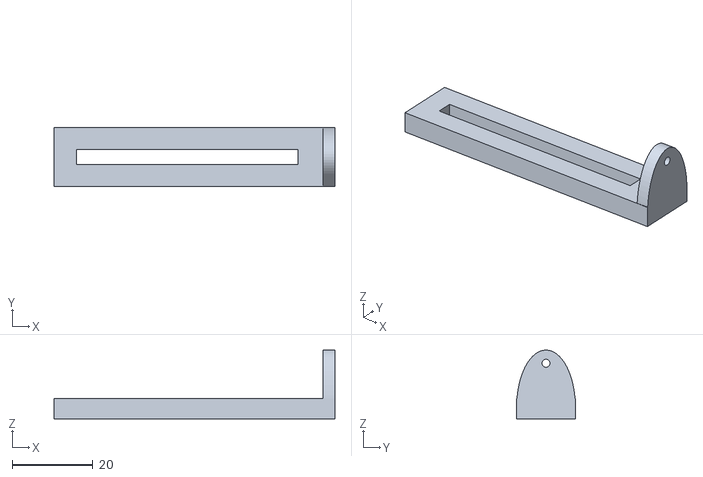
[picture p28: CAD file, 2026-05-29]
HeadFixed_Setup/WaterDelivery/Water_delivery_3d_models/linear_actuator_rackbody_singlespout (1).stl
69.4 x 14.5 x 17.0

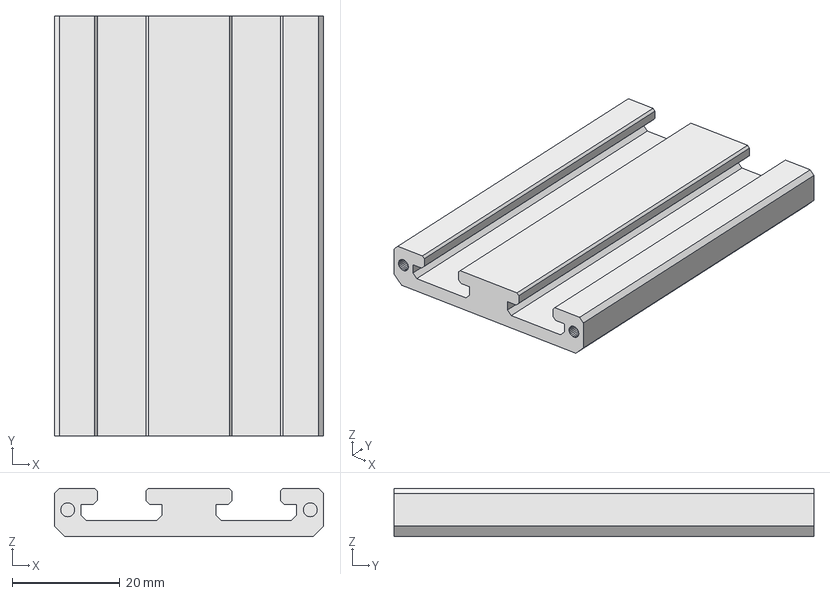
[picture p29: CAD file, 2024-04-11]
ReachingBox_3D_Model/Feeder V2/XYstage_Rail.FCStd
50.0 x 78.0 x 9.00 mm

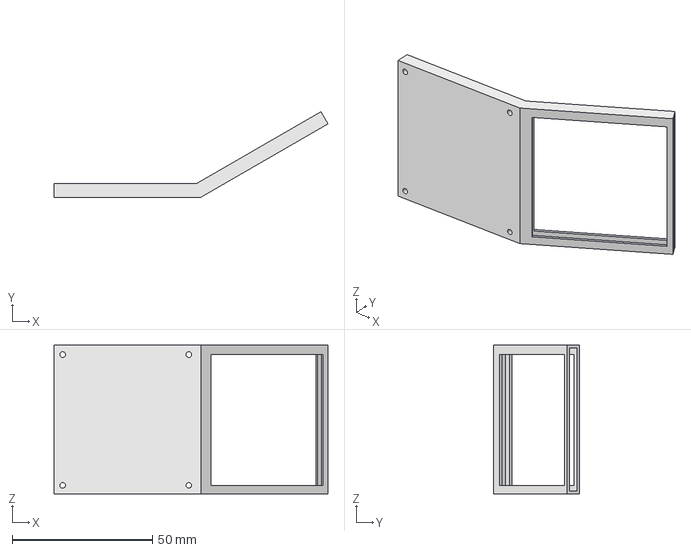
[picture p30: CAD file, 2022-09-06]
ReachingBox_3D_Model/Hinge for the mirror.FCStd
97.7 x 30.5 x 53.0 mm

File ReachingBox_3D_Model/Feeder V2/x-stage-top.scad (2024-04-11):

M3 = 1.65;
M3F = 1.8;
M3H = 3.1;
LGR = 1.2;

TXB = 10;
TYB = 10;

module top_plate(){
	difference(){
		cube(size=[35,35,3], center=true);

		translate([TXB,TYB,0]) cylinder(r=M3, h=10, center=true);
		translate([-TXB,-TYB,0]) cylinder(r=M3, h=10, center=true);
		translate([TXB,-TYB,0]) cylinder(r=M3, h=10, center=true);
		translate([-TXB,TYB,0]) cylinder(r=M3, h=10, center=true);

		cylinder(r=M3, h=10, center=true);
	}
}

module side(){
	difference(){
		cube(size=[35,4,9], center=true);

		translate([13,0,1.5]) rotate([90,30,0]) cylinder(r=LGR, h=50, $fn=6, center=true);
		translate([-13,0,1.5]) rotate([90,30,0]) cylinder(r=LGR, h=50, $fn=6, center=true);

		translate([0,0,1.5]) rotate([90,30,0]) cylinder(r=M3F, h=50, $fn=12, center=true);
		translate([0,3.5,1.5]) rotate([90,0,0]) cylinder(r=M3H, h=5, $fn=6, center=true);

	}
}

union(){
	top_plate();
	translate([0,4,3.5]) side();
	translate([0,-4,3.5]) rotate([0,0,180]) side();

}

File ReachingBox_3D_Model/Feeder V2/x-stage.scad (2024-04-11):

M3 = 1.65;
M3F = 1.8;
M3H = 3.5;
LGR = 1.2;

TYB = 10;
TXB = 10;

module foundation(){
	difference(){
		cube(size=[35,35,3], center=true);

		translate([TXB,TYB,0]) cylinder(r=M3, h=10, center=true);
		translate([-TXB,-TYB,0]) cylinder(r=M3, h=10, center=true);
		translate([TXB,-TYB,0]) cylinder(r=M3, h=10, center=true);
		translate([-TXB,TYB,0]) cylinder(r=M3, h=10, center=true);

		translate([TXB,TYB,1.5]) cylinder(r=M3H, h=3, center=true);
		translate([-TXB,-TYB,1.5]) cylinder(r=M3H, h=3, center=true);
		translate([TXB,-TYB,1.5]) cylinder(r=M3H, h=3, center=true);
		translate([-TXB,TYB,1.5]) cylinder(r=M3H, h=3, center=true);

		cylinder(r=M3, h=10, center=true);
		translate([0,0,1.5]) cylinder(r=3.5, h=3, center=true);

	}
}

module side(){
	difference(){
		cube(size=[35,4,9], center=true);

		translate([13,0,2]) rotate([90,30,0]) cylinder(r=LGR, h=50, $fn=6, center=true);
		translate([-13,0,2]) rotate([90,30,0]) cylinder(r=LGR, h=50, $fn=6, center=true);

		translate([0,0,2]) rotate([90,30,0]) cylinder(r=M3F, h=50, $fn=12, center=true);
	}
}

union(){
	foundation();
	translate([0,15.5,3]) side();
	translate([0,-15.5,3]) side();

}

// +1.5 
// -5.5 + 3 = -2.5
// -2.5 + 11 = 8.5
// -1.5 + 11 = 9.5
//  9.5 - 1.5 = 8
//  9.5 / 2 = 4.75

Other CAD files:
ReachingBox_3D_Model/Reaching Box/FrontWall.FCStd
ReachingBox_3D_Model/Reaching Box/Reaching box blueprint.FCStd
HeadFixed_Setup/Headplate_designs/large holder (1) (2).STL
HeadFixed_Setup/WaterDelivery/Water_delivery_3d_models/delivery_base (1).stl
HeadFixed_Setup/Headplate_designs/3 hole_y shaped (1).3MF
HeadFixed_Setup/Headplate_designs/3 hole_y shaped (1).STEP
HeadFixed_Setup/Headplate_designs/3 hole_y shaped (1).STL
HeadFixed_Setup/Headplate_designs/headplate-1 (1).3MF
HeadFixed_Setup/Headplate_designs/headplate-1 (1).STEP
HeadFixed_Setup/Headplate_designs/headplate-1 (1).STL
HeadFixed_Setup/Headplate_designs/headplate.3MF
HeadFixed_Setup/Headplate_designs/headplate.stl
HeadFixed_Setup/Headplate_designs/holder-Body002.3MF
HeadFixed_Setup/Headplate_designs/holder-Body002.STEP
HeadFixed_Setup/Headplate_designs/large holder (1).3MF
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

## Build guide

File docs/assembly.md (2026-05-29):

---
layout: page
title: Behavioral apparatus
nav_order: 2
description: "This is a description of ReachOut behavioral box"

---

## Behavioral box design
Current protocol is performed with the use of in-house manufactured behavioral box system, which consists of multiple components: 
- Plexiglas chamber with a metal bar floor and a slit in the front wall, housing the mouse during the experiment; 
- Motorized feeder system for precisely delivering and positioning single pellets (5-10 mg Sucrose Tap Pellets, TestDiet) in front of the slit;
- Arduino-based controller autonomously performing the programmed experimental protocol (written in C++), interfacing with the touch sensors in the box and providing the master clock signal;
- Single FLIR 1.6MP High-Speed camera (Model: Blackfly S BFS-U3-16S2M) with a system of mirrors, saving the video stream on the computer with the use of a Python interface.

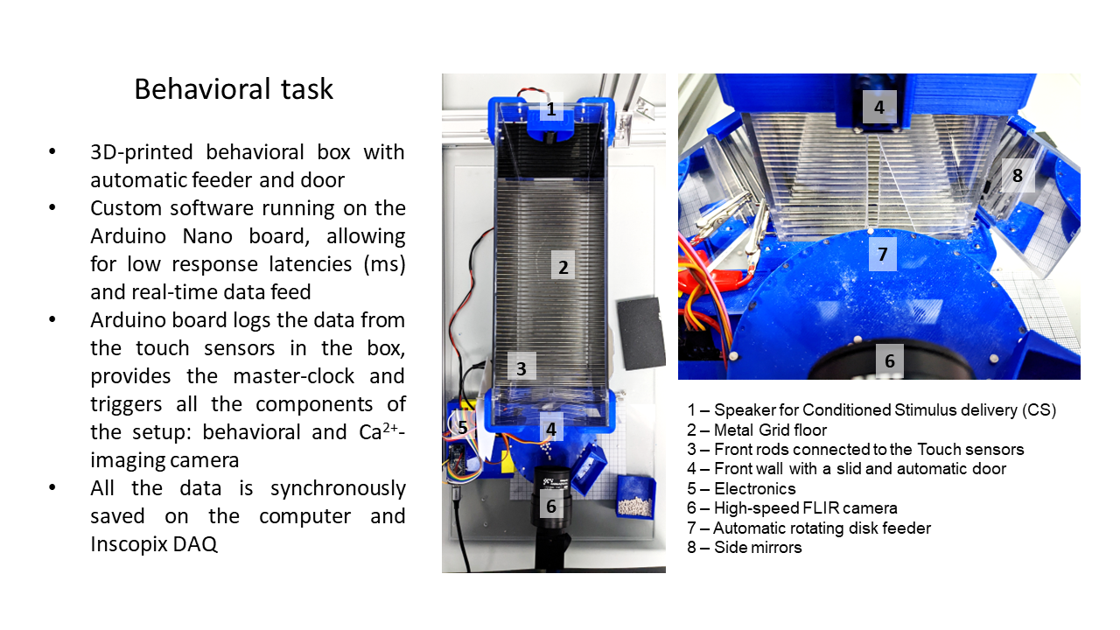
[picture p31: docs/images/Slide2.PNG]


Hence, there are **4 main components that you will need** to assemble the behavioral box: 

- Plexiglas sheets cut to size and drilled 
- 3d printed parts for the box such as corners holding the sheets together,
- 3d printed feeder and Arduino components
- Small screws and nuts kit to put everything together and metal rods for the floor (can be ordered from Amazon) 

All of them can be purchased or manufactured in house with the use of 3d printer and CNC machines or just ordered online.

## 3D printing the parts

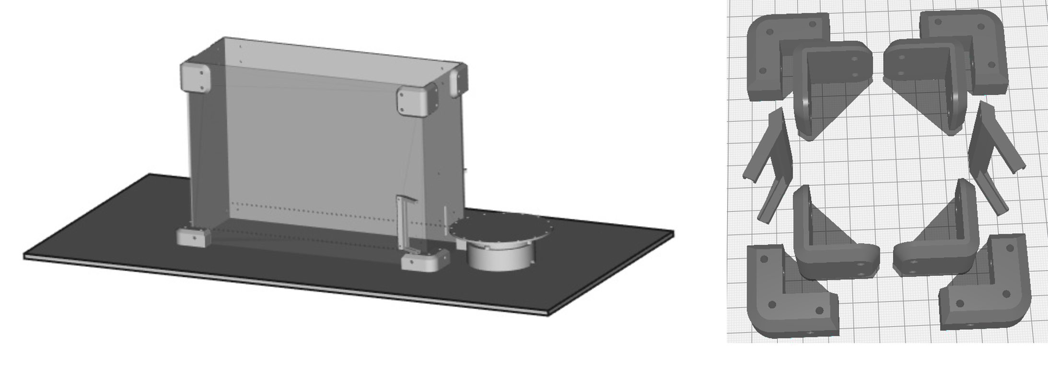
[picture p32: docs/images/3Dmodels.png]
  

*.stl* files for printing the components are provided in [this folder] of the repository. 
Dimensions for the parts and schematics is provided in [supplementary materials] of the repository and [the article].
Computer-aided design (CAD) software along with CNC cutter machine can be used to scale and speed up the manufacturing process 
(all the design files provided were made using [FreeCAD] software), but the original design can be easily reproduced without it using only all-manual tools.  

## Q&A
If you still have questions after reading this and [the article] please let us
know and we list it in this section.

[this folder]: https://github.com/BerezhnoyD/Reaching_Task_VAI/tree/main/ReachingBox_3D_Model
[FreeCAD]: https://www.freecad.org/
[supplementary materials]: https://github.com/BerezhnoyD/Reaching_Task_VAI/tree/main/ArticleSupplements
[the article]: https://star-protocols.cell.com/protocols/3539

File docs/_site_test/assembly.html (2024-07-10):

Skip to main content

ReachOut kinematic analysis

This site uses Just the Docs (https://github.com/just-the-docs/just-the-docs), a documentation theme for Jekyll.

## Behavioral box design

Current protocol is performed with the use of in-house manufactured behavioral box system, which consists of multiple components:

- Plexiglas chamber with a metal bar floor and a slit in the front wall, housing the mouse during the experiment;
- Motorized feeder system for precisely delivering and positioning single pellets (5-10 mg Sucrose Tap Pellets, TestDiet) in front of the slit;
- Arduino-based controller autonomously performing the programmed experimental protocol (written in C++), interfacing with the touch sensors in the box and providing the master clock signal;
- Single FLIR 1.6MP High-Speed camera (Model: Blackfly S BFS-U3-16S2M) with a system of mirrors, saving the video stream on the computer with the use of a Python interface.



Hence, there are 4 main components that you will need to assemble the behavioral box:

- Plexiglas sheets cut to size and drilled
- 3d printed parts for the box such as corners holding the sheets together,
- 3d printed feeder and Arduino components
- Small screws and nuts kit to put everything together and metal rods for the floor (can be ordered from Amazon)

All of them can be purchased or manufactured in house with the use of 3d printer and CNC machines or just ordered online.

## 3D printing the parts



.stl files for printing the components are provided in this folder (https://github.com/BerezhnoyD/Reaching_Task_VAI/tree/main/ReachingBox_3D_Model) of the repository. Dimensions for the parts and schematics is provided in supplementary materials (https://github.com/BerezhnoyD/Reaching_Task_VAI/tree/main/ArticleSupplements) of the repository and the article (https://star-protocols.cell.com/protocols/3539). Computer-aided design (CAD) software along with CNC cutter machine can be used to scale and speed up the manufacturing process (all the design files provided were made using FreeCAD (https://www.freecad.org/) software), but the original design can be easily reproduced without it using only all-manual tools.

## Q&A

If you still have questions after reading this and the article (https://star-protocols.cell.com/protocols/3539) please let us know and we list it in this section.

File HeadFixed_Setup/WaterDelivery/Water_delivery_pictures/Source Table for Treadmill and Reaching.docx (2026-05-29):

REAGENT or RESOURCE | SOURCE | IDENTIFIER | PRICE
Specific vendor parts
Mouse Head Fixation System | https://www.labeotech.com/product/mouse-head-fixation/ | | 500$
10ml Syringes
Silicone tubing and connectors
Blunt needles
Amazon parts
M3 long screws as shafts
M6 long screw as shaft
Veroboard
Nema 17 motor
BYJ48 12V motor
Servo motor
LED
Speaker
12V stepper motor shield
Nema motor shield
Arduino Nano
Touch Sensor
Custom parts
3D printed XYZ actuator parts
3D printed water pump parts

Head-fixed Reaching Setup

The following table describes all the parts that you need to assemble the head-fixed reaching setup. It includes off the shelf parts as well as custom manufactured details. Further details can be found in a step-by-step assembly guide

Head-fixed Treadmill Setup

The following table describes all the parts that you need to assemble the head-fixed treadmill setup, similar to one found in this STARs protocol (https://pubmed.ncbi.nlm.nih.gov/36107745/). It includes off the shelf parts as well as custom manufactured details. Further details can be found in a step-by-step assembly guide

REAGENT or RESOURCE | SOURCE | IDENTIFIER | PRICE
Specific vendor parts
Thorlabs
Right-Angle Clamp for Ø1/2" Posts, 5 mm Hex | Thorlabs | RA90/M | 10.82$ x 4
Rotating Clamp for Ø1/2" Posts, 360° Continuously Adjustable, 5 mm Hex | Thorlabs | SWC/M | 27.45$ x 2
Ø12.7 mm Optical Post, SS, M4 Setscrew, M6 Tap, L = 75 mm | Thorlabs | TR75/M | 6.15$ x 10
Ø1/2" Pedestal Post Holder, Spring-Loaded Hex-Locking Thumbscrew, L=2.19" | Thorlabs | PH2E | 28.5$ x 4
150 mm x 300 mm x 12.7 mm Aluminum Breadboard, M6 Double-Density Taps | Thorlabs | MB1530/M | 158$
Clamping Fork for Ø1.25" Pedestal Bases, 31.5 mm Counterbored Slot, M6 x 1.0 Captive Screw | Thorlabs | CF125C/M | 13$ x 4
Large V-Clamp with PM4/M Clamping Arm, 63.5 mm Long, Metric | Thorlabs | VC3C/M | 45.15$
Amazon parts
Optical encoder HEDR-5420-ES214 | https://www.amazon.com/HEDR-5420-ES214-Encoders-Channel-200-Refltve/dp/B01IOX7EBW | Broadcom ASIN: B01IOX7EBW | 60$
Magnetic rotary encoder Taiss for 6 mm shaft, 360 Pulses per Rotation | https://www.amazon.com/Taiss-Incremental-Encoder-Voltage-Warranty%EF%BC%89600P/dp/B07MWZ4CLT/ref=sr_1_3?crid=2KVPUVLWE4XO3&dib=eyJ2IjoiMSJ9.kRs6eEqxELK-TM6RGACHYxmNA_MXwOl_jKs_jX3zJP6dgDGARN1EH_bI0PdceGShmyXwwOwJWA8SrokZexOqMD3ViyUWmVYI8fOmZ8lMcYMAJSGpkp7zW3gPgSqpfdl3Z0CgjYzNgKDsrY4ONUy-wnS9qcYEHsi5yNg0mfV5w_34DKw1bvS3D_kzMBIGJQ7ZxWHlNEMB9yGrX1jptRMyO82BnVZkpzvHuO74VtyOORk.z3qkB5hSRxK_rZQsX0vhMfX8iWzXcxsx_fpw8jedsnE&dib_tag=se&keywords=rotary%2Bencoder&qid=1747078219&sprefix=rotary%2Bencoder%2Caps%2C54&sr=8-3&th=1 | Taiss UPC: 760412050429 | 20$ x 2
2pcs 6 to 6mm flexible shaft coupling connector | https://www.amazon.com/Befenybay-Aluminium-Flexible-Coupling-Connector/dp/B07YYZ54KJ/ref=sr_1_4?crid=2OPSR2MKL0KEC&dib=eyJ2IjoiMSJ9.C7nSsOIR9JITuSuY2vJBrkNQFhQrf0QH6zcxW9kNfvEK5saeY7OhHzveB-Ik6I9kyJ0tS2sQaJYeCEuMKLmkPb_DtDV3FNjSygWV5BWsi6oIGbVIDVvWyz4KwgRwx8281IRyMF7SGiRGbMz7U0sIaBwGqM0pQA8roR2FQ0lXFkGmo_uDtrT2xrrv7BUnZf7pe2Ev4K40KfDG4cfrztbdqssNwW3C0rT_XsbaQvZbPn8.HATJLBBIli9HPj-DOsC7Pe2ZNY-M8qM_YL8Mp1sPgvw&dib_tag=se&keywords=shaft%2Bmotor%2Bcoupler&qid=1747082808&sprefix=shaft%2Bmotor%2Bcoupler%2Caps%2C73&sr=8-4&th=1 | | 13$

Uxcell Two side Linear ball bearings 6mm

https://www.amazon.com/uxcell-LMH6UU-Flange-Linear-Bearings/dp/B07H97FZMY/ref=sr_1_26?crid=1FG40AXVP8R2Y&dib=eyJ2IjoiMSJ9.83UBnbNSSi3pI4AD3mSf7seOgrZK_c26l7Z4FiLKg8P8_VDybvkwk7_qmNZ0F7tJxN6UmmkjP9Yq7gAHoKxeY1x7joc8jxEuuEQT8unjY3SbdDklGwZYmC284Mf1jOM0Zxm57gGvEfhxcGeTKNc4aNH_lxE1cUhM77j2c3G3C0cV32hnqXAk4nm6TDBF-d88kksq8bFRSJ99xKqD0P4SzIN5JTJTMbwvf6rxEwp131gjWRYJFA5qYgatKmVbZ-WfYgdBQV6BItNaCNj-jHZ3K93reEvylxC-iwDHA6gqo7o.ZeItc3U5H3X9uDFJIJjw6JYlERCYhsJuxr5NfDDEPwg&dib_tag=se&keywords=6mm%2Bshaft%2Bwith%2Bbearings&qid=1747151851&s=industrial&sprefix=6mm%2Bshaft%2Bwith%2Bbearings%2Cindustrial%2C49&sr=1-26&th=1

Uxcell

13$

5pcs Stanless steel D-shaft 6mm

https://www.amazon.com/Stainless-D-Shaft-Linear-Industrial-Gobilda/dp/B08QJSVXDD/ref=sr_1_30?crid=1FG40AXVP8R2Y&dib=eyJ2IjoiMSJ9.83UBnbNSSi3pI4AD3mSf7seOgrZK_c26l7Z4FiLKg8P8_VDybvkwk7_qmNZ0F7tJxN6UmmkjP9Yq7gAHoKxeY1x7joc8jxEuuEQT8unjY3SbdDklGwZYmC284Mf1jOM0Zxm57gGvEfhxcGeTKNc4aNH_lxE1cUhM77j2c3G3C0cV32hnqXAk4nm6TDBF-d88kksq8bFRSJ99xKqD0P4SzIN5JTJTMbwvf6rxEwp131gjWRYJFA5qYgatKmVbZ-WfYgdBQV6BItNaCNj-jHZ3K93reEvylxC-iwDHA6gqo7o.ZeItc3U5H3X9uDFJIJjw6JYlERCYhsJuxr5NfDDEPwg&dib_tag=se&keywords=6mm+shaft+with+bearings&qid=1747151851&s=industrial&sprefix=6mm+shaft+with+bearings%2Cindustrial%2C49&sr=1-30

15$

Pillow Block Bearing for 6mm shaft

https://www.amazon.com/Pillow-Block-Bearing-12-7mm-Diameter/dp/B09ZRWHNKF/ref=sr_1_20?crid=1FG40AXVP8R2Y&dib=eyJ2IjoiMSJ9.83UBnbNSSi3pI4AD3mSf7seOgrZK_c26l7Z4FiLKg8P8_VDybvkwk7_qmNZ0F7tJxN6UmmkjP9Yq7gAHoKxeY1x7joc8jxEuuEQT8unjY3SbdDklGwZYmC284Mf1jOM0Zxm57gGvEfhxcGeTKNc4aNH_lxE1cUhM77j2c3G3C0cV32hnqXAk4nm6TDBF-d88kksq8bFRSJ99xKqD0P4SzIN5JTJTMbwvf6rxEwp131gjWRYJFA5qYgatKmVbZ-WfYgdBQV6BItNaCNj-jHZ3K93reEvylxC-iwDHA6gqo7o.ZeItc3U5H3X9uDFJIJjw6JYlERCYhsJuxr5NfDDEPwg&dib_tag=se&keywords=6mm%2Bshaft%2Bwith%2Bbearings&qid=1747151851&s=industrial&sprefix=6mm%2Bshaft%2Bwith%2Bbearings%2Cindustrial%2C49&sr=1-20&th=1

9$
High Density foam roller | https://www.amazon.com/Prosource-Density-Therapy-Balance-Exercises/dp/B01696AOH2/ref=sr_1_1?crid=OCBQNLUU5BO4&dib=eyJ2IjoiMSJ9.8PCgKfoC4lyXQA0h6oqaZLTO4C1TBa9ZPVyYZvB65e16h-L3ivz2iUqpAvIZZC0OXNvH87L5rJ0fOCtH8zT5Bc7YsUaH3zVT6zxlOzyOMyQc51NmnEqCodLY_5PCzuHIJGeISyv4IrrcM4EzERMO1CXmtVBVHKh0ZJA9AIu8KnxdUgYPiE1karsyDzKI2y_Gt2ROkXSFOi9re3ej--kH0eaFRXLArb4vRZPEm0ddSvg.F2ObDejDBs9pFbqbUYJiEdLBk_Ei4xYtcV1dD3y1fvE&dib_tag=se&keywords=roller%2Bpost%2Bhigh&qid=1747152235&sprefix=roller%2Bpost%2Bh%2Caps%2C273&sr=8-1&th=1 | | 16$
Mechanical XY moveable stage | https://www.amazon.com/Mechanical-Moveable-Microscope-Caliper-Precision/dp/B07VPQT851/ref=sr_1_6?crid=18NMKBXYV76LT&dib=eyJ2IjoiMSJ9.VoJQyZe8ZR5tl2C4gKwx5l-rzFgtu9WWT8EQoFLJCKHYZ06_51ZPdTQ5BCIfyhBD2pRVvzxaqIE61XKuaibjyrfnkUjIIXaaPzpFNYGuEFrux6EVigStgyjxLIKzpoZNAN1OL1NHwYbJirxNwWf_AQjClnmf9HMCfrpPkYN_FXSfHrIH6WHJifTCBl_nnd2PPNA3mnuo13m6TK04Pq2Ew92SX2soEEfUqGRJeQyeqqE.t1E3kq9qCyjJxpG7B2ZJKjZR8znAyHIHjHO2Y9qoEt8&dib_tag=se&keywords=microscope+xy+stage&qid=1747237194&sprefix=microscope+xy+stage%2Caps%2C61&sr=8-6 | | 20$
Custom parts
3D printed baseplate holders | | | 10$/100$ depends on material
3D printed headbar holders | | | 10$/100$ depends on material
Custom headplates | Order from SendCutSend | | 40$

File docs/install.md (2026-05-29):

---
layout: page
title: Software Installation
parent: Software part
nav_order: 5
description: "This is a description of ReachOut software installation"
---

## Installation
### Recording toolbox
The recording toolbox contains two parts: 
- one on the **Arduino** side 

```
Choose one of the provided scripts, edit and upload to the microcontroller with the use of Arduino IDE
```

- and one on the **PC** side. This one is just the snippet to record from the FLIR camera and simultaneously record from Arduino.
The second part is taken with minor changes from the [PySpin] repository, so you should follow the installation instructions listed there.

> INSTALLATION: Most of the dependencies in the import statements are included in a standard Anaconda installation (i.e. PIL, Numpy, Tkinter) 
> and with your NVIDIA graphics card (i.e CUDA) for the GPU versions. PySpin and the Spinnaker API must be downloaded from the FLIR website (https://www.flir.com/products/spinnaker-sdk/);
> choose the appropriate version of Spinnaker and install first, then install the "Latest Python Spinnaker" version that is compatible with your version of Python (I've tested with Python 3.5 & 3.8) 
> using the instructions in the ReadMe file. An FFMPEG executable needs to be downlaoded (https://ffmpeg.org/download.html) and placed in a folder that you can point to in the import statements, 
> such as within the site-packages folder of your Python installation. Finally, scikit-video (http://www.scikit-video.org/stable/) can be added to your Python installation using pip.

After installing PySpinCapture simply run one of the scripts provided in the [ReachOut] repository [Recording Toolbox] like that:

```python
> cd path\to\the repository\
> python CameraRoll.py
```

### Analysis toolbox
Analysis toolbox included with this project can be used as a part of the proposed [STARs Protocols] pipeline or as a standalone application
The analysis toolbox is dependent on certain python libraries and programs (DEEPLABCUT, ANIPOSE) and Jupyter Notebook.
To make it easier for installation all the dependencies are included in the updated *DEEPLABCUT.yml conda environment file
contained in [ReachOut] repository [Analysis Toolbox].
After installing Anaconda just run the following commands:

```python
> cd path\to\the repository\Analysis toolbox\
> conda env create -f DEEPLABCUT.yml
```

## Q&A

If you still have questions after reading this and [STAR Protocols] please let us
know and we list it in this section. If you experience any bugs during the installation or
use please let us know ASAP so we can fix them in the next release. We appreciate your feedback

---

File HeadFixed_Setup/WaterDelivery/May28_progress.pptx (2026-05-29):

## Daniil Berezhoi data update

May 28

## Head fixation and treadmill system

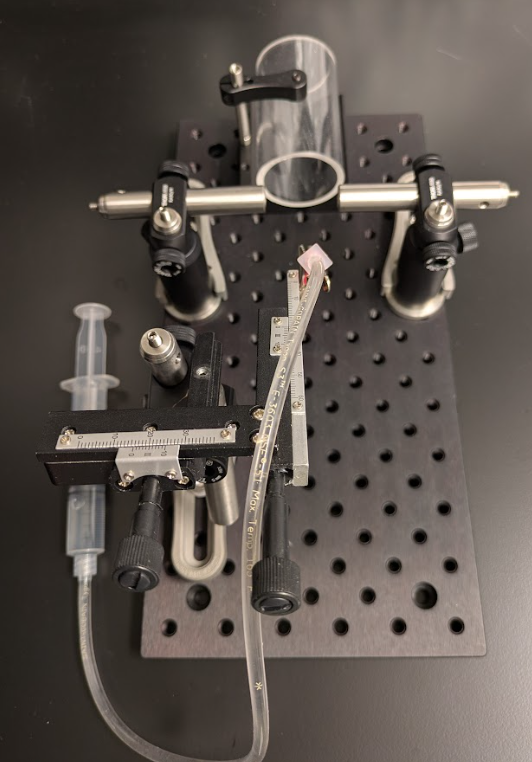
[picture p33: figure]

Manual positioner

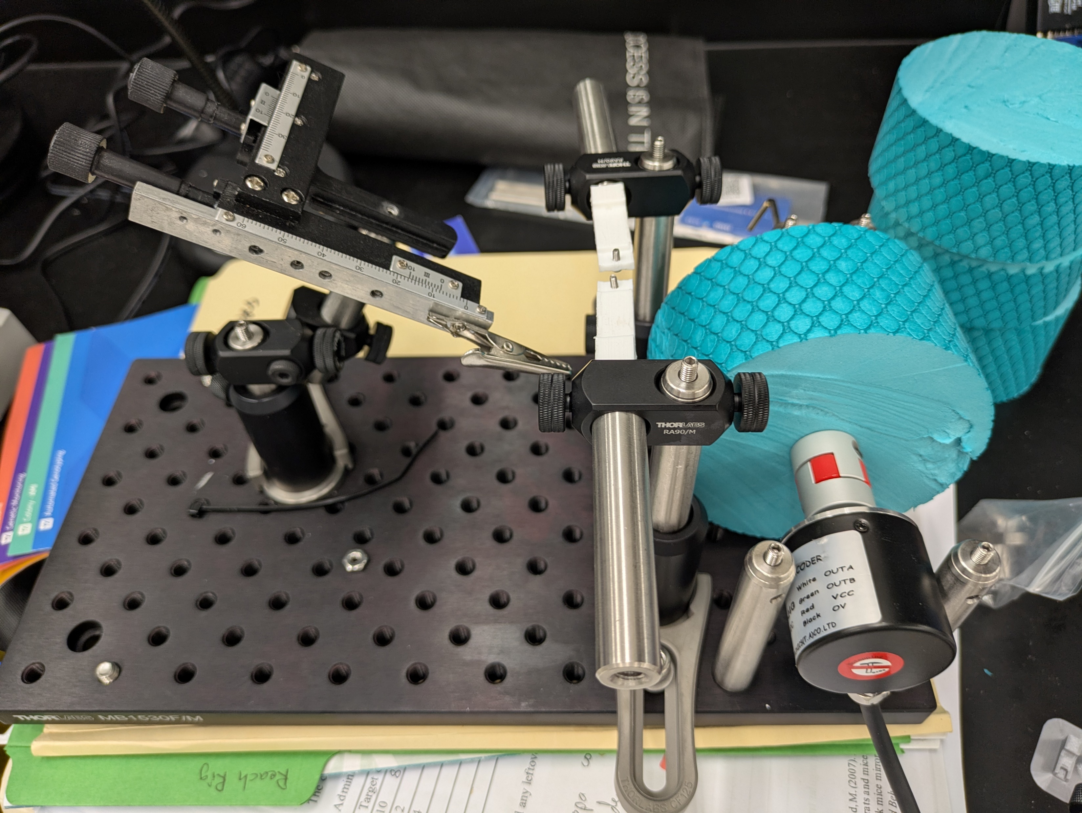
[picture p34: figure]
Изображение выглядит как инструмент, машина, пластик, дрель Контент, сгенерированный ИИ, может содержать ошибки.
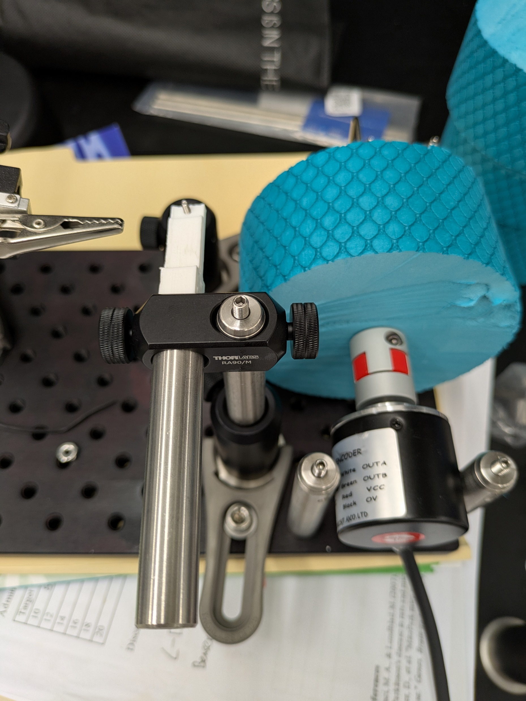
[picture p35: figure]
Изображение выглядит как инструмент, дрель, в помещении Контент, сгенерированный ИИ, может содержать ошибки.

## Animal training

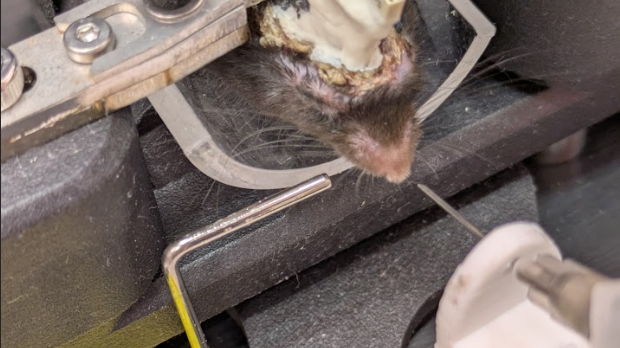
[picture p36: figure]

Sound - CS

Habituation

Water - CR

Sound - CS

Initial training

Water - CR

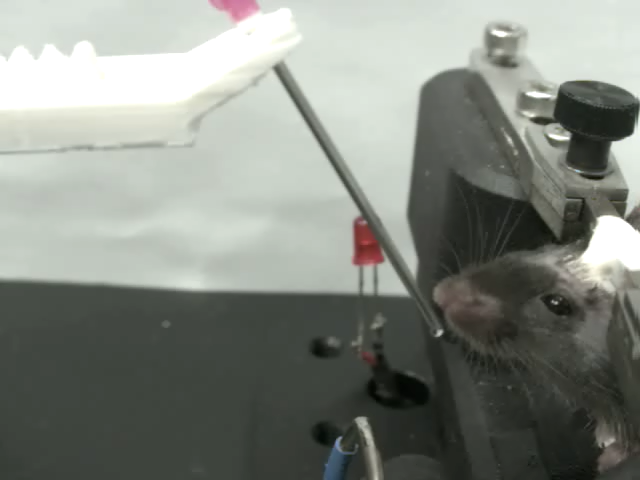
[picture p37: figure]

Sound - CS

CS training

Water - CR

Delay training

Sound - CS

Water - CR

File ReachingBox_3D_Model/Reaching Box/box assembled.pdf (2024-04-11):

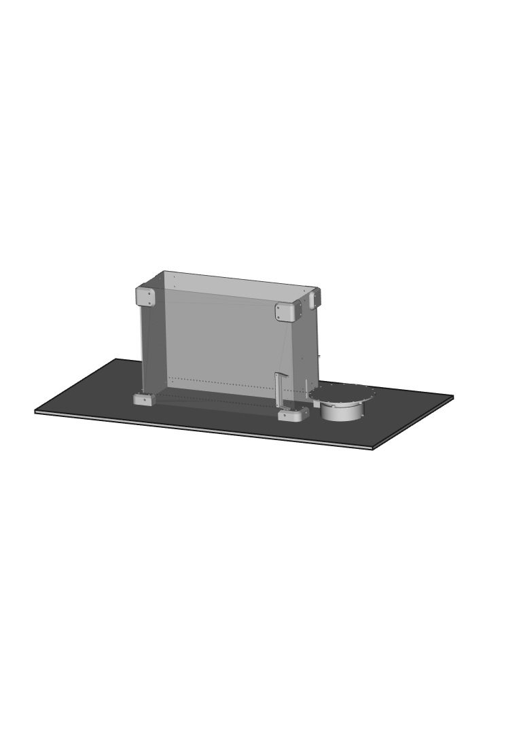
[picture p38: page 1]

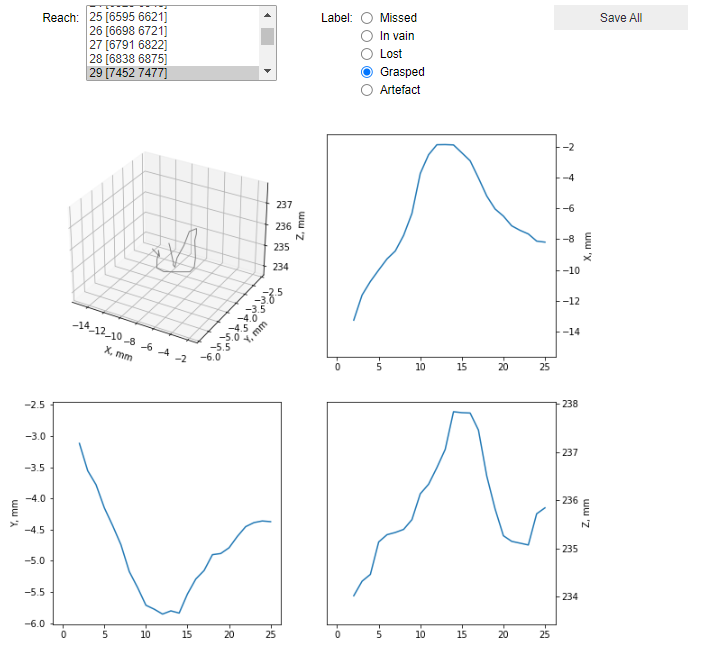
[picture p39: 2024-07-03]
docs/_site_test/images/Step4.png

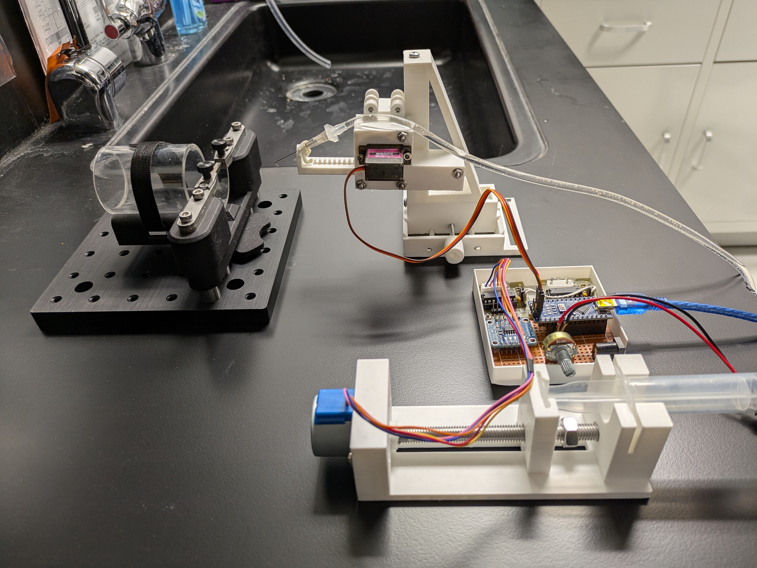
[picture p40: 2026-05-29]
HeadFixed_Setup/WaterDelivery/Water_delivery_pictures/PXL_20250227_234422202.jpg

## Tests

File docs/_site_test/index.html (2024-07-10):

Skip to main content

ReachOut kinematic analysis

This site uses Just the Docs (https://github.com/just-the-docs/just-the-docs), a documentation theme for Jekyll.



ReachOut project is an open-source hardware-software platform for analyzing reaching movement kinematics in mice. The whole design consists of 3 main parts described here:

- 3D printed box for training mice to perform reach-to-grasp task & acquire behavioral videos for kinematic analysis
- Arduino-based controller for executing behavioral protocol & recording animal behavior
- ReachOut software (analysis pipeline) to analyze videos & perform kinematic analysis on reconstructed forepaw trajectory

 (https://zenodo.org/doi/10.5281/zenodo.7383917)

There is an Article in STAR Protocols with all the details and Repository on GitHub with all materials to recreate the setup

View it in the Article (https://star-protocols.cell.com/protocols/3539) View it on GitHub (https://github.com/BerezhnoyD/Reaching_Task_VAI/)

This website documents the features of the current main branch accompanying the STARs Protocol article. For the code described in the article use alpha or beta release in the ReachOut (https://github.com/BerezhnoyD/Reaching_Task_VAI/) repository

### Getting Started

Did you know that mice are pretty good at using their forepaws? Well, probably you do and can skip the Science background section and go straight to Project overview or to one of the sections provided in the docs (Navigation on the left sidebar).



But how to dissect and study this complex movement? We tried to provide the comprehensive solution to this problem that can be implemented in-lab with a little background knowledge in 3d printing, Arduino and Python Coding.

All the installation instructions are currently in the Software part section. You can use the analysis part separately for your project by copying the Jupyter Notebooks.

### Science background

Reach-to-grasp task in rodents first developed by Ian Whishaw ¹ has recently became the gold standard for the study of fine motor behavior in rodents. The structure of the movement and the neurocircuitry behind it can be well translated between rodents and higher primates including humans ²³ which makes this task very popular for the study of cortical motor control. There is an increasing use of reach-to-grasp task along current neurophysiological tools like 2-photon imaging or optogenetics for the study of neural activity during execution of the planned motor command ⁴. However, there are not many designs available for the reach-to-grasp task in freely behaving mice.

With the dawn of DIY electronic kits (Arduino) and stereolithography 3D printer technology (OpenCAD) we see the field of open-source behavioral box design rapidly expanding and being a major driver for neuroscience discoveries. There are multiple designs for Skinner boxes and rodent operant chambers proposed by different laboratories. However, there are fewer solutions to study fine motor skills, probably due to the difficulties in precise presentation of the reinforcement and quantifying the kinematics of the small animal movements. The second problem has been recently solved with the use of deep-learning video analysis DeepLabCut (https://github.com/DeepLabCut/DeepLabCut/). However, the solutions specifically tailored for the behavior-neurophysiology coupling often use head-fixed animals and focused on precise synchronization of the animal behavior, heavily constrained, with the neurophysiology recording. Training animals in such setups can be problematic and labor-intensive. On the other side, apparatuses proposed to study reaching in freely behaving animals, following the line of operant boxes research, usually lack the precision and time resolution needed to synchronize with external devices used in neurophysiology research. Moreover, research with automatic learning boxes, even ReachingBots ⁵, generally focus on simple metrics like the number of trials and success rate of reaching and overlook more sophisticated kinematic analysis which requires better video quality, precision and post-processing of the behavioral data. Thus, there is always a tight balance between the open-source (ease of manufacture) and research-grade (temporal precision) needed for neurophysiology and precise kinematic studies.

Trying to fill this gap we have developed a comprehensive hardware-software setup for mice, using the current state-of-the-art solutions in 3D printing and DNN data analysis and made it accessible to the large open-science community.

### Project overview

This website describes the basics of design, fabrication, assembly and use case for the open-source hardware platform for mice reach-to-grasp task training and fine motor skill video analysis. You are free to use either the Software part of this project for kinematic analysis (ReachOut pipeline) on the videos from your setup or build the whole behavioral apparatus setup using the instructions provided in the STAR Protocols (https://star-protocols.cell.com/protocols/3539) article.

Behavioral apparatus - automated mouse Reaching Box that is 3D printed and hence easily reproducible. The device is used to train animals to perform reach-to-grasp dexterity task: approach the proximal part of the reaching box and reach for single sugar pellets disposed by motorized feeder disk located in front of the narrow slit. This task is used for studying planning and execution of fine motor skills requiring cortical control of the forepaw and finger movement. The semi-automated setup allows to record the video and track the forepaw and fingers during the reaching movement.

Hardware used in the design of the task, aside from the high-speed FLIR camera, consists of readily available open-source components that can be acquired relatively cheap or fabricated with the use of stereolithography 3D printer.

The ReachOut (https://github.com/BerezhnoyD/Reaching_Task_VAI/) repository contains all the materials to build the mouse reaching task and analyze the data acquired with this task

- 3D models for the components of the box
- Schematics for the reaching box Arduino-based controller
- Scripts to run the video recording from the FLIR Camera and logging the data from Arduino
- Scripts for the full analysis dataflow: detecting body parts with DLC and getting the reaching trajectories

Analysis software can be used with the behavioral box to analyze reaching kinematics or as a standalone application for kinematic analysis for the action of your choice (walking, whisker movement, you name it) in your project with certain adaptations. The aim of this part is to simplify keypoint tracking (performed by DLC networks), reviewing tracking results along with the videos and extract different kinematic parameters (speed, acceleration, jerk, accuracy) and different moments of the reach (start, peak, end) to use them as behavioral keypoints (ex. peri-event analysis).

We gathered all the code in a series of annotated Jupyter Notebooks for you to use. All the necessary libraries can be installed using provided DEEPLABCUT.yml environment file for Anaconda. For the quick overview and instructions go straight to Software part section.

## About the project

ReachOut is maintained © 2022-2024 by Daniil Berezhnoi (https://www.researchgate.net/profile/Daniil-Berezhnoy). All the materials are OpenSource and Authors would be happy to help you with any questions on the code.

1. The structure of skilled forelimb reaching in the rat: A proximally driven movement with a single distal rotatory component (https://www.sciencedirect.com/science/article/pii/016643289090053H). ↩
2. Post-stroke kinematic analysis in rats reveals similar reaching abnormalities as humans (https://www.nature.com/articles/s41598-018-27101-0) ↩
3. Quantitative kinematic characterization of reaching impairments in mice after a stroke (https://pubmed.ncbi.nlm.nih.gov/25323462/) ↩
4. Online control of reach accuracy in mice (https://www.ncbi.nlm.nih.gov/pmc/articles/PMC7814908/) ↩
5. ReachingBot: An automated and scalable benchtop device for highly parallel Single Pellet Reach-and-Grasp training and assessment in mice (https://www.sciencedirect.com/science/article/pii/S0165027023001279?via%3Dihub) ↩

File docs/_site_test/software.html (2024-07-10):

Skip to main content

ReachOut kinematic analysis

This site uses Just the Docs (https://github.com/just-the-docs/just-the-docs), a documentation theme for Jekyll.

# Triangulation and analysis of behavioral videos



In addition to the hardware part, we provide the complementary software data analysis pipeline which can be performed off-line with the acquired videos. Python package for the 3d trajectory reconstruction and kinematic analysis is organized in classes and modules implemented in a series of Jupyter Notebooks and based on the state-of-the-art solutions for the markerless pose estimation as well as original code

- DeepLabCut (https://github.com/DeepLabCut/DeepLabCut) is used for intial tracking using pretrained ResNet architecture (& training it).
- Anipose Lib (https://github.com/lambdaloop/anipose) is used for the 3d triangulation part to restore the action in absolute coordinates (mm).
- ReachOut (https://github.com/BerezhnoyD/Reaching_Task_VAI/) is our humble code contribution and is used for all the analysis on kinematic traces.

## ReachOut kinematic analysis pipeline

The ReachOut (https://github.com/BerezhnoyD/Reaching_Task_VAI/) pipeline can be used separately on your own videos and guides the user through the number of steps to extract the parts from the video, track and triangulate the points of interest (paw, fingers), cluster the reaches, visualize and compare basic kinematic parameters for different reaching categories. User has the ability to export the final data on the kinematics (scalars for each reach) and reaching timestamps as a *.h5/.csv table for further analysis or synchronization with his own pipeline.



Analysis pipeline consists of extracting the parts from the video, tracking and triangulating the points of interest (paw, fingers), clustering the reaches, visualizing and comparing basic kinematic parameters between different reaching categories. We suggest copying the whole folder

- 2D pipeline or
- 3D pipeline

from the Analysis Toolbox (https://github.com/BerezhnoyD/Reaching_Task_VAI/tree/main/Analysis%20toolbox), nd then running the Notebooks using Jupyter

> cd path\to\the scripts\
> conda activate DEEPLABCUT
> jupyter notebook

## Using ReachOut analysis pipeline

There are two pipelines provided - one for 3d analysis and reconstruction, and a simpler 2d one, working with only one video (single camera view). We mention the differences in the following sections and suggest to start with a simpler one if your experiment doesn’t specfically require triangulation and representation of coordinates in absolute space (in mm).

The Notebooks are split by their function: ReachOut - Tracking guides the user throught the necessary steps for tracking the points of interest

- Cutting the video acquired with FLIR camera into three parts - specific for our setup with two mirrors
- Opening the DeepLabCut interface window and running through the full pipeline to track the points of interest
- Updating the csv output from DeepLabCut with absolute position for our reference points
- Using the code from Anipose lib and preprecorded calibration videos to triangulate the points - specific for our setup with two mirrors



Here are the main steps as described in the Notebooks

### ReachOut - Tracking

**Provides all the scripts to process the behavioral videos and get to the .csv file with **



1. Cut the video from the FLIR camera into three parts - three different views of the reach
  We are recording the videos of the reaching task using the single high speed widefield FLIR camera and multiple mirrors. So the first part is to cut single video into parts corresponding to the Rightside view (CamA), Center view (CamB), Leftside view (CamC) with respect to the animal paw. This eliminates the need for synchronisation of different videos, but adds this additional step before we can analyze our videos with DLC. As a result of this step you should get three video files with the names -camA, -camB, -camC
2. Analyze the video with DeepLabCut
  This step is performed using open-source DeepLabCut (https://github.com/DeepLabCut/DeepLabCut) package, the tutorial and more info on which can be found on GitHub. In short, the first command should launch DeepLabCut interface which guides you through creating the network, training dataset from your videos (selecting subset of frames and manually labeling the points of interest), training & evaluating the network and finally applying it to all your videos. The final output should be a .csv file for each video with coordinates (in pixel dimensions) for all the points tracked by the network. We added some code to open, check this table and insert necessary columns with static points for triangulation.

It should be further noted that despite the Anipose documentation advice to use single DLC network for all views we found that better results are achieved with two separate networks trained on the side(1) and front(2) view. That means we start DLC analysis for our videos twice - first time for all the CamA/C videos, and the second time for CamB. As a result we get two separate sets of *.csv *.h5 files. For the next step they should have the same name with the difference of last prefix “A,B,C” and copied together to one folder accessible by this Notebook. Not needed if using simpler 2D pipeline without triangulation

1. Triangulate the 2d trajectories with Anipose and check the quality of the 3d trajectory
  This step is done using the open-source Anipose package, so the tutorial and more info on them can be found on GitHub Here we provide the code snippet (from Anipose Lib (https://github.com/lambdaloop/anipose)) to calibrate the camera intrinsics using prerecorded videos or checkerboard pattern and use the resulting calibration.toml file to triangulate coordinates for the paw in absolute space.
  If you want to use Anipose interface for triangulation you should manually put the resulting .csv and .h5 files into anipose project folder */Anipose project/pose-2d before before starting the triangulation command anipose triangulate
  As a result of this step you should get the single *.csv file for each session, containing absolute x,y,z coordinates, that we will use further Not needed if using simpler 2D pipeline without triangulation

### ReachOut - Analysis

Provides multiple gui snippets to manually segment and annotate the results from DeepLabCut



- Manually scroll through DeepLabCut tracking coordinates, plot them and choose the segments for kinematic analysis (reaches in our case)
- Load the selected parts of the trajectory and manually annotate them from watching the corresponding parts of the video (we defined different reaching categories)
1. Open the .csv file, scroll through the trajectories and manually choose the fragments of the trajectory (with the reaches) for analysis
  This script will ask you to choose a file with the OpenFile interface. Point it to the *.csv file generated by the previous notebook. It will open the GUI to review the 2d trajectory with time used as a 3rd dimension and extract the fragments of the trajectory for further analysis. As a result of this step you will have the *.h5 file with the fragments of the trajectory that you’ve chosen. Open this file to review the trajectories.

Small video showing the workflow

In cotrast to the standard 3D pipeline (tracking_split), 2D relies on the different script (tracking_split_2d), all other steps are the same, but with the time substituting Z-dimension in the 3D plot, that way you basically see the change in 2d trajectory with time.

1. Open the h5 file and the corresponding video to review and classify the trajectories
  This script is made to load the selected parts of the trajectory and manually annotate them from watching the corresponding parts of the video. For this script to work point it to the *.h5 file you want to analyze (file) and the video corresponding to the same session (file2.mp4) and then use the GUI to rewatch the video fragments and manually assign the labels. As a result of this step you will have the *scalars.h5 file which is used in the vizualisation steps 5 and 6.

### ReachOut - Visualization

Provides the user with multiple ways to visualize the data and kinematic parameters



- Look at superimposed trajectories for the chosen category of action - reaches in our case
- Look at the violin plots for different kinematic parameters for the chosen category of action
- Cluster the actions based on the chosen set of parameters
1. Open the scalars.h5 file and plot all the trajectories of the chosen category
  This snippet shows all reaches in the chosen category as Timeseries for visual inspection and analysis. From the lists you can choose the category of reaches and the type of data to plot.



1. Open the scalars.h5 file and make violin plots for the chosen parameters and reach categories



1. Open the scalars.h5 file and automatically cluster the reaches using one of the built in methods
2. Show the number of reaches in each category

## Q&A

If you still have questions after reading this and STAR Protocols (https://star-protocols.cell.com/protocols/3539) please let us know and we list it in this section.

## Table of contents

- Software Installation

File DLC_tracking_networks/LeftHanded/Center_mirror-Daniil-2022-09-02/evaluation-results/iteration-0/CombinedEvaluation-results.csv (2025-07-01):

 | Training iterations: | %Training dataset | Shuffle number | Train error(px) | Test error(px) | p-cutoff used | Train error with p-cutoff | Test error with p-cutoff
0 | 700000 | 95 | 1 | 1.64 | 5.56 | 0.6 | 1.64 | 5.56

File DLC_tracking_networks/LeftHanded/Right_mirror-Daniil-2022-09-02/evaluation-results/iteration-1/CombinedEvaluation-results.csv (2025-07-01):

 | Training iterations: | %Training dataset | Shuffle number | Train error(px) | Test error(px) | p-cutoff used | Train error with p-cutoff | Test error with p-cutoff
0 | 1000000 | 95 | 2 | 1.03 | 3.69 | 0.6 | 1.03 | 3.69
1 | 1000000 | 95 | 1 | 1.44 | 2.98 | 0.6 | 1.44 | 2.98

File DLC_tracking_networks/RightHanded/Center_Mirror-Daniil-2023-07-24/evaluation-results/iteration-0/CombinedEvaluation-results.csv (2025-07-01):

 | Training iterations: | %Training dataset | Shuffle number | Train error(px) | Test error(px) | p-cutoff used | Train error with p-cutoff | Test error with p-cutoff
0 | 1000000 | 95 | 1 | 1.79 | 4.69 | 0.6 | 1.79 | 4.69

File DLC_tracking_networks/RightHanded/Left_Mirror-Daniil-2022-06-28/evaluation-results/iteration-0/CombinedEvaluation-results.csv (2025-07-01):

 | Training iterations: | %Training dataset | Shuffle number | Train error(px) | Test error(px) | p-cutoff used | Train error with p-cutoff | Test error with p-cutoff
0 | 1000000 | 90 | 2 | 1.19 | 2.45 | 0.6 | 1.19 | 2.42
1 | 1000000 | 90 | 1 | 1.18 | 1.3 | 0.6 | 1.18 | 1.3
2 | 300000 | 90 | 1 | 1.76 | 6.83 | 0.6 | 1.76 | 6.83

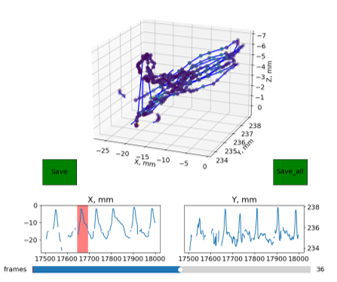
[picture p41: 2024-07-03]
docs/_site_test/images/Picture6.png

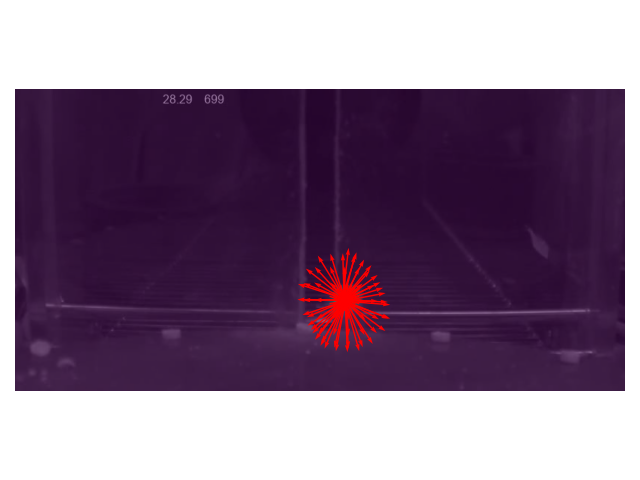
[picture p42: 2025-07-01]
DLC_tracking_networks/LeftHanded/Center_mirror-Daniil-2022-09-02/evaluation-results/iteration-1/Center_mirrorSep2-trainset95shuffle2/maps/img00699.png_locref_train_2_0.95_snapshot-1000000.png

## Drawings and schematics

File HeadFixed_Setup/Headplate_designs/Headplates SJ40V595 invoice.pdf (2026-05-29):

# Quote

# SJ40V595

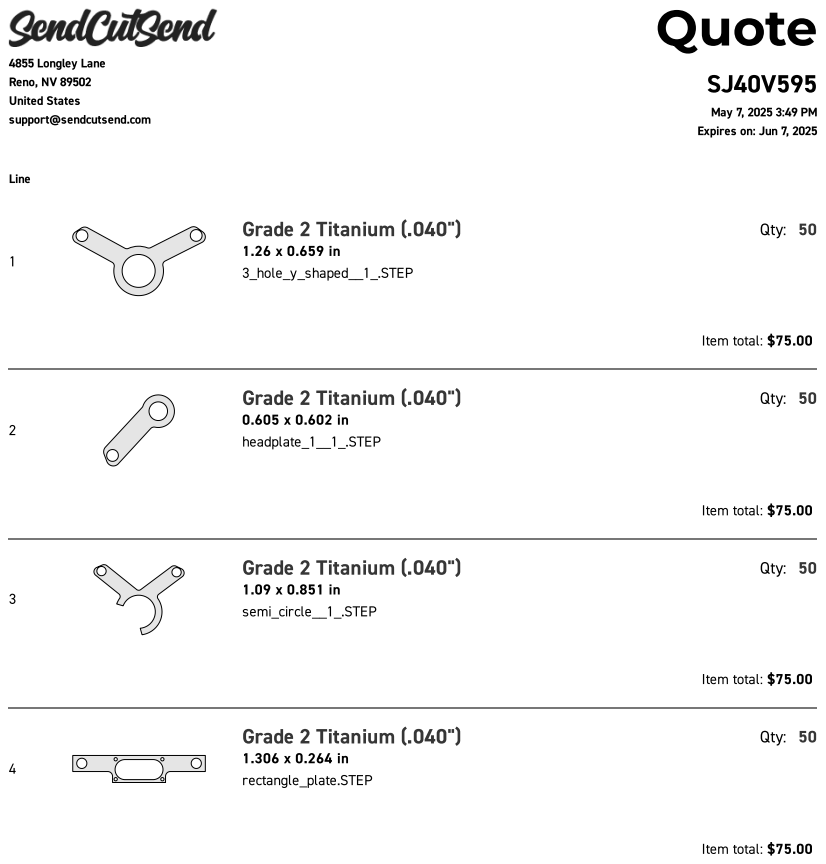
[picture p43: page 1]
Line; Grade 2 Titanium (.040"); 3_hole_y_shaped__1_.STEP; Qty: 50; Item total: $75.00; headplate_1__1_.STEP; semi_circle__1_.STEP; rectangle_plate.STEP

4855 Longley Lane
Reno, NV 89502
United States
support@sendcutsend.com

May 7, 2025 3:49 PM
Expires on: Jun 7, 2025

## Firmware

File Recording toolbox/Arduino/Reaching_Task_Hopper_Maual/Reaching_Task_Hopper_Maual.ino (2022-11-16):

// REACHING TASK CONTROL PROGRAM
// This Arduino program is designed for the Simple mouse reaching task in the Dr.Chu lab by Daniil Berezhnoi, 03/28/22
// It is capable of receiving data from two Sensors - input Pins - and controlling three instances - output Pins - based
// on those readings. Upon receiving the presence signal from the Sensor 1 (inPin1) it switches ON the Conditioned Stimulus (outPin1)
// and if animal reacts to the conditioned stimulus by pressing a Sensor 2 (inPin2) it turns the Feeder Stepper motor (motorPins) and
// triggers the Gate Servo motor (outPin2) to open the feeder. It also sends the Synchro signal (outPin3) to trigger FLIR camera and Logs
// the data in a serial port.


// Including Libraries
#include <Bounce2.h>
#include <Stepper.h>
#include <Servo.h>
#define BOUNCE_WITH_PROMPT_DETECTION

// Setting the constants
const int stepsPerRevolution = 2048;  // Change this to fit the number of steps per revolution if you are using the motor different from 28BYJ-48
const int motorPins[] = {2, 4, 3, 5}; // Feeder pins
const int inPin1 = 9;     // SENSOR1 pin
const int inPin2 = 10;     // SENSOR2 pin
const int inPin3 = 8;      // SENSOR3 pin
const char inPin4 = A0;     // FLIR_SYNC_PIN
const int ButPin1 = A1;     // SENSOR2 pin
const int ButPin2 = A2;     // SENSOR2 pin

const int outPin1 = 6;      // SPEAKER pin
const int outPin2 = 7;      // GATE pin
const int outPin3 = 12;      // SYNCHRO pin
const int outPin4 = 13;     // TICKING pin

// Here go all the latencies in the protocol   
const int debounceDelay3 = 1000; // the duration of the Food availability
const int but_delay1 = 500; // the latency in ms for the first sensor to be triggered   - !!! DETERMINES THE TIME ANIMAL SHOULD STAY IN FRONT !!!
const int but_delay2 = 500; // the latency in ms for the second sensor to be triggered  - !!! DETERMINES THE TIME ANIMAL SHOULD HOLD THE BAR !!!

// All other variables
const int Timing = 1; // Timing of the program in ms
unsigned long cur_time = 0;  
unsigned long lastDebounceTime2 = 0; 
int reading1 = 0;
int reading2 = 0;
int reading3 = 0;
int reading4 = 0;
int but1_reading = 0;
int but2_reading = 0;
int Speaker = 0;
int Gate = 1;
int Reinforcement = 0;
int Sync = 0;
int pos = 15;    // variable to store the servo position

// Creating components-instances
Stepper myStepper(stepsPerRevolution, motorPins[0], motorPins[1], motorPins[2], motorPins[3]); // That's a Feeder motor and Pins it's connected to
Servo myServo;                                     // That's a Servo motor for controling the door
Bounce debouncer1 = Bounce();                      // That's a debouncers used to track only continuous sensor touches (see debouncer.interval)
Bounce2::Button debouncer2 = Bounce2::Button();    // That's a debouncers used to track only continuous sensor touches (see debouncer.interval)
Bounce debouncer3 = Bounce();
Bounce debouncer4 = Bounce();

void setup() {
// This code runs only once once when the Device starts
  myStepper.setSpeed(5); // Speed for the stepper motor, controling feeder.         !!! CAN BE ADJUSTED !!!
  myServo.attach(outPin2); // Attaching the gate to the GATE pin
  
  pinMode(outPin1, OUTPUT); // Setting the inputs/outputs
  pinMode(outPin2, OUTPUT);
  pinMode(outPin3, OUTPUT);
  pinMode(outPin4, OUTPUT);
  pinMode(inPin3, INPUT_PULLUP);
  debouncer1.attach(inPin1, INPUT_PULLUP); // See debouncer
  debouncer1.interval(but_delay1);  // The length of staying in front
  debouncer2.attach(inPin2, INPUT_PULLUP); // See debouncer
  debouncer2.interval(but_delay2);  // The length of grabbing the bar
  debouncer2.setPressedState(LOW);
  debouncer3.attach(ButPin1, INPUT_PULLUP); // See debouncer - Button for the feeder rotation
  debouncer3.interval(50);  
  debouncer4.attach(ButPin2, INPUT_PULLUP); // See debouncer - Button for the feeder rotation
  debouncer4.interval(50);  
  Serial.begin(115200);               // Starting the data logging
  digitalWrite(outPin1, LOW);
  myServo.write(pos);               // Setting the initial possition for the gate
}

void loop() {
  // This code runs repeatedly and controls the experiment continuously
  digitalWrite(outPin4, HIGH);    // Tick when the code starts
  debouncer1.update();            // Reinitializing the debouncers
  debouncer2.update();
  debouncer3.update();
  debouncer4.update();
  reading1 = debouncer1.read();   // Monitoring the inputs from Sensors
  reading2 = debouncer2.read();
  reading3 = digitalRead(inPin3);
  reading4 = analogRead(inPin4);  // Monitoring the input from FLIR  

  but1_reading = debouncer3.read();   // Monitoring the inputs from buttons
  but2_reading = debouncer4.read();
  
  Reinforcement = 0;

    if (but2_reading == 0 && (millis() - lastDebounceTime2) > debounceDelay3){   // HANDLING THE ROTATION OF THE FEEDER
          Reinforcement = 1;
          myStepper.step(stepsPerRevolution/16);          // One step of the Stepper motor        - !!! FEEDER TURNS !!!
          lastDebounceTime2 = millis(); 
    }

    if (but1_reading == 0 && (millis() - lastDebounceTime2) > debounceDelay3){   // HANDLING THE ROTATION OF THE FEEDER
          Reinforcement = 1;
          myStepper.step(-stepsPerRevolution/16);          // One step of the Stepper motor        - !!! FEEDER TURNS !!!
          lastDebounceTime2 = millis(); 
    }


    if ((millis() - cur_time) > Timing){                                                                              // LOGGING THE DATA
        cur_time = millis(); // Getting Timestamp from the beginning of the program
        digitalWrite(outPin4, LOW);    // Tick when the code ends
        Serial.print(cur_time);   // Timestamp
        Serial.print(" ");   
        Serial.print(reading1);   // Sensor1
        Serial.print(" ");   
        Serial.print(Speaker);    // Speaker
        Serial.print(" ");   
        Serial.print(reading2);   // Sensor2
        Serial.print(" "); 
        Serial.print(reading3);   // Sensor3
        Serial.print(" ");
        Serial.print(reading4);   // FLIR
        Serial.print(" ");   
        Serial.print(Gate);     // Gate
        Serial.print(" ");   
        Serial.print(Reinforcement);     // Reinforcement
        Serial.print(" ");   
        Serial.println(Sync);     // Sync
    }

}

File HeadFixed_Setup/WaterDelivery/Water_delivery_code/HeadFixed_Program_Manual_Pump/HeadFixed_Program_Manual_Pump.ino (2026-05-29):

// REACHING TASK CONTROL PROGRAM
// This Arduino program is designed for the Simple mouse reaching task in the Dr.Chu lab by Daniil Berezhnoi, 03/28/22
// It is capable of receiving data from two Sensors - input Pins - and controlling three instances - output Pins - based
// on those readings. Upon receiving the presence signal from the Sensor 1 (inPin1) it switches ON the Conditioned Stimulus (outPin1)
// and if animal reacts to the conditioned stimulus by pressing a Sensor 2 (inPin2) it turns the Feeder Stepper motor (motorPins) and
// triggers the Gate Servo motor (CS_sync_Pin) to open the feeder. It also sends the Synchro signal (outPin3) to trigger FLIR camera and Logs
// the data in a serial port.


// Including Libraries
#include <Bounce2.h>
#include <Servo.h>
#include <Stepper.h>

#define BOUNCE_WITH_PROMPT_DETECTION

#define STEPS 200

// Setting the constants
//const int motor1Pins[] = {3, 4, 5, 6}; // Motor1 pins
const int motorPin1 = 3;
const int motorPin2 = 4;
const int motorPin3 = 5;
const int motorPin4 = 6;
const int delivery_sync_Pin = 8;
const int potpin = A7;
const int inPin1 = 2;     // BUTTON1/SENSOR1 pin
const int inPin2 = 12;     // SENSOR2 pin
const int outPin1 = 11;      // MOTOR spout attenuator pin
const int outPin2 = 9;       // NEMA motor pin1 
const int outPin3 = 10;      // NEMA motor pin2
const int CS_sync_Pin = 13;      // SYNCHRO pin
const int CSpin = 7;



// Here go all the latencies in the protocol   
const int but_delay1 = 100; // the latency in ms for the first sensor to be triggered   - !!! DETERMINES THE TIME ANIMAL SHOULD HOLD THE BAR FOR THE WATER TO DISPENSE !!!
const int but_delay2 = 1000; // the latency in ms for the second sensor to be triggered  - !!! DETERMINES THE SPEED OF THE REACTION TO THE SPOUT TOUCH !!!
const int CS_length = 10000; // the duration of the CS beep sound  
const int Frequency = 5000;

// All other variables
const int Timing = 1; // Timing of the program in ms
unsigned long cur_time = 0;  
unsigned long lastDebounceTime1 = 0; 
const int delayTime = 2; // Speed of the syringe motor
const int steps = 30; // Number of steps to control the pump
const int Number_Steps = 50; // Number of steps to control the pump (Nema)

int reading1 = 0;
int reading2 = 0;
int Speaker = 0;
int Reinforcement = 0;
int Sync = 0;
int val;
int pos = 15;    // variable to store the servo position

// Creating components-instances

Servo myServo;                                     // That's a Servo motor for controling the drinking spout position
Bounce debouncer1 = Bounce();                      // That's a debouncers used to track only continuous sensor touches (see debouncer.interval)
Bounce2::Button debouncer2 = Bounce2::Button();    // That's a debouncers used to track only continuous sensor touches (see debouncer.interval)

Stepper stepper(STEPS, outPin2, outPin3);
#define motorInterfaceType 1

void setup() {
// This code runs only once once when the Device starts
  
  stepper.setSpeed(100);
  myServo.attach(outPin1); // Attaching the motor to the SPOUT pin
  debouncer1.attach(inPin1, INPUT_PULLUP); // See debouncer
  debouncer1.interval(but_delay1);  // The length of staying in front
  debouncer2.attach(inPin2, INPUT_PULLUP); // See debouncer
  debouncer2.interval(but_delay2);  // The length of grabbing the bar
  debouncer2.setPressedState(LOW);


  pinMode(outPin1, OUTPUT); // Setting the inputs/outputs
  pinMode(CS_sync_Pin, OUTPUT);
  pinMode(motorPin1, OUTPUT);
  pinMode(motorPin2, OUTPUT);
  pinMode(motorPin3, OUTPUT);
  pinMode(motorPin4, OUTPUT);
  pinMode(delivery_sync_Pin, OUTPUT);
  pinMode(CSpin, OUTPUT);
  Serial.begin(115200);               // Starting the data logging
  
}

void loop() {
  // This code runs repeatedly and controls the experiment continuously
  debouncer1.update();            // Reinitializing the debouncers
  debouncer2.update();
  digitalWrite(delivery_sync_Pin, LOW);

  reading1 = debouncer1.read();   // Monitoring the inputs from Sensors
  reading2 = debouncer2.read();
  val = analogRead(potpin);
  val = map(val, 0, 1023, 0, 180);
  myServo.write(val);               // Setting the initial possition for the spout
  Reinforcement = 0;

  if (Speaker == 0 && Reinforcement == 0 && reading1 == 0) {  // CONDITIONED STIMULI ONSET
    tone(CSpin, Frequency);
    digitalWrite(CS_sync_Pin, HIGH);  // SYNCHRO pin gets high
    Sync = 1;
    Speaker = 1;
    lastDebounceTime1 = millis();
     
    }
  
  if (Speaker == 1 ){                                       // HANDLING THE OFFSET OF CONDITIONED STIMULI 
      if ((millis() - lastDebounceTime1) > CS_length){ // WHEN TIME ELAPSES
      noTone(CSpin);                                      // Switching off the CS with time - !!! CS OFF AFTER DESIGNATED TIME !!! 
      digitalWrite(CS_sync_Pin, LOW);                           // SYNCHRO pin gets low
      Speaker = 0;                                          
      Sync = 0;
      }
    }

  if (reading2 == 0 && Speaker == 1){   // HANDLING THE ROTATION OF THE SYRINGE PUMP MOTOR - NOT THE BEST WAY AS THE FUNCTION IS BLOCKING, NEED TO REWRITE USING STEPPER LIBRARY IF IT PROVIDES THE SAME TORQUE OR DRIVE PATTERN AS HERE
        noTone(CSpin);
        digitalWrite(CS_sync_Pin, LOW);
        Reinforcement = 1;
        Speaker = 0;                                          
        Sync = 0;

        digitalWrite(delivery_sync_Pin, HIGH);
        stepper.step(Number_Steps);

        for (int x = 0; x < steps; x++) {
          digitalWrite(motorPin1, LOW);
          digitalWrite(motorPin2, LOW);
          digitalWrite(motorPin3, LOW);
          digitalWrite(motorPin4, HIGH);
          delay(delayTime);
          digitalWrite(motorPin1, LOW);
          digitalWrite(motorPin2, LOW);
          digitalWrite(motorPin3, HIGH);
          digitalWrite(motorPin4, HIGH);
          delay(delayTime);
          digitalWrite(motorPin1, LOW);
          digitalWrite(motorPin2, LOW);
          digitalWrite(motorPin3, HIGH);
          digitalWrite(motorPin4, LOW);
          delay(delayTime);
          digitalWrite(motorPin1, LOW);
          digitalWrite(motorPin2, HIGH);
          digitalWrite(motorPin3, HIGH);
          digitalWrite(motorPin4, LOW);
          delay(delayTime);
          digitalWrite(motorPin1, LOW);
          digitalWrite(motorPin2, HIGH);
          digitalWrite(motorPin3, LOW);
          digitalWrite(motorPin4, LOW);
          delay(delayTime);
          digitalWrite(motorPin1, HIGH);
          digitalWrite(motorPin2, HIGH);
          digitalWrite(motorPin3, LOW);
          digitalWrite(motorPin4, LOW);
          delay(delayTime);
          digitalWrite(motorPin1, HIGH);
          digitalWrite(motorPin2, LOW);
          digitalWrite(motorPin3, LOW);
          digitalWrite(motorPin4, LOW);
          delay(delayTime);
          digitalWrite(motorPin1, HIGH);
          digitalWrite(motorPin2, LOW);
          digitalWrite(motorPin3, LOW);
          digitalWrite(motorPin4, HIGH);
          delay(delayTime);
    }
  }



  if ((millis() - cur_time) > Timing){                                                                              // LOGGING THE DATA
      cur_time = millis(); // Getting Timestamp from the beginning of the program
      Serial.print(cur_time);   // Timestamp
      Serial.print(" ");   
      Serial.print(reading1);   // Sensor1
      Serial.print(" ");   
      Serial.print(reading2);   // Sensor2
      Serial.print(" ");   
      Serial.print(Reinforcement);     // Reinforcement
      Serial.print(" ");   
      Serial.print(val);     // Angle of the spout actuator
      Serial.print(" ");   
      Serial.println(Sync);     // Sync
  }

}

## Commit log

2024-04-11 Add files via upload
    Added printable models and CAD files for all the components of the box
    [BackWall-BodyPad.stl, BackWall.FCStd, Box assembled.FCStd, Disc feeder-Compound.stl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]
2025-07-01 Added the DLC networks
    Added the latest (July 2023) used snapshots for the DeepLabCut networks trained on the data from the ReachOut box.
    [CollectedData_Daniil.csv, CombinedEvaluation-results.csv, DLC_resnet50_Center_MirrorJul24shuffle1_1000000-results.csv, DLC_resnet50_Center_mirrorSep2shuffle1_7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]
2026-05-27 Add HeadFixed Setup
    [3 hole_y shaped (1).3MF, 3 hole_y shaped (1).STEP, 3 hole_y shaped (1).STL, headplate-1 (1).3MF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]
2026-05-29 Re-upload a website and HeadFixed part
    [3 hole_y shaped (1).3MF, 3 hole_y shaped (1).STEP, 3 hole_y shaped (1).STL, Zstage-Fusion (1).stl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]

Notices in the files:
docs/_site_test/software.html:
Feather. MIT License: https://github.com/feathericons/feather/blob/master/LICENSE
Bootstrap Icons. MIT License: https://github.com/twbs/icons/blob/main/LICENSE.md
